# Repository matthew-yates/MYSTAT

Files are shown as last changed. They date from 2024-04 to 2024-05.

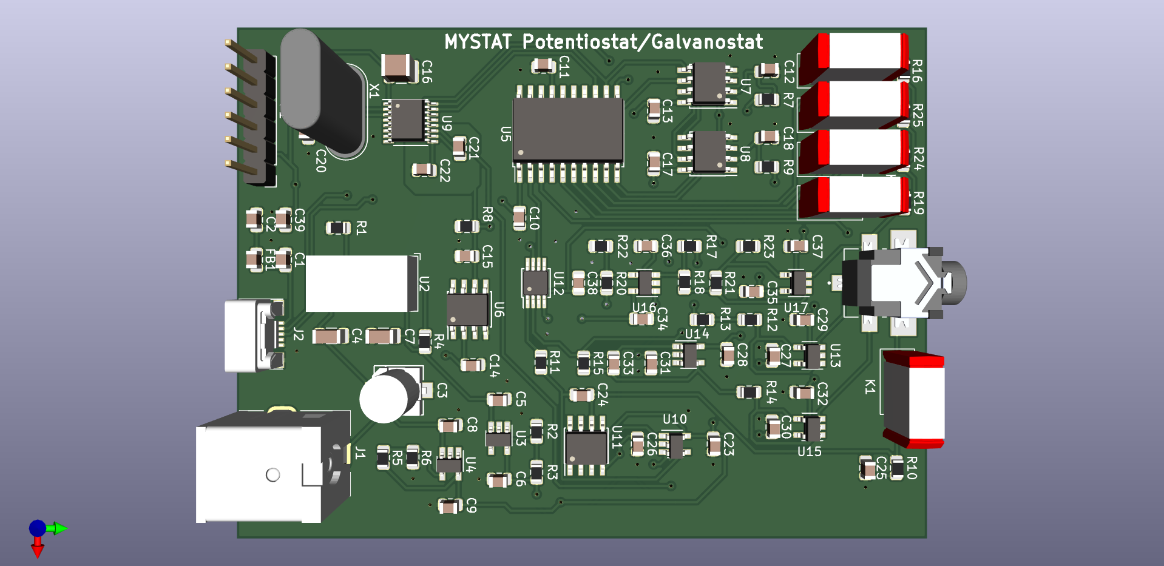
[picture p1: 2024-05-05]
hardware/mystat_circuit_board/mystat.png

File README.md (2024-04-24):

## MYSTAT Potentiostat/Galvanostat

These are the design files for building and operating a compact open source potentiostat/galvanostat instrument.  The detailed technical specifications and instructions for operation can be found in the HardwareX article [MYSTAT: A compact potentiostat/galvanostat for general electrochemistry measurements](https://www.hardware-x.com/article/S2468-0672(20)30072-9/fulltext). The HardwareX article has a link to a static repository at [Zenodo](https://zenodo.org/records/4252476).  This github repository was created as a clone of the Zenodo repository, with the goal of facilitating the tracking of improvements to hardware design and development of control software.

The MYSTAT instrument design and control software is based on an earlier open source design published by [Thomas Dobbelaere](https://www.hardware-x.com/article/S2468-0672(17)30031-7/fulltext), who also created a [github repository](https://github.com/thomasdob/tdstatv3) for that instrument.

The voltage and current ranges of MYSTAT are significantly higher than the original design of Dobbelaere. The printed circuit board was completely redesigned. Only relatively minor changes were made to the Python control software and microcontroller firmware originally created by Dobbelaere.

This hardware and control software is fully open source, and changes/improvements are welcome.  An entirely open source tool chain was used for its development (KiCad, Python, and Linux).

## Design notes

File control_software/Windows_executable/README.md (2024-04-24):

This Windows executable version of the control software includes Python 3 and all the supported libraries and modules needed.  The libusbK Windows device driver must also be installed.  Windows version 7 or later is required.

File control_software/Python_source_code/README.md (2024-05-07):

### Setup instructions for Python virtual environment

The current version of mystat.py is incompatible with the latest version of pyqtgraph.  As a workaround, set up a virtual environment that uses pyqtgraph version 0.12.4.  The code below can be followed to set up the virtual environment in the same directory (folder) that you have saved the file "mystat.py".

```
python3 -m venv venv
source venv/bin/activate
pip install pyqtgraph==0.12.4
pip install scipy
pip install PyQt5
pip install pyusb
deactivate
```

For Linux: To give users the ability to control the potentiostat without root permissions, make sure that the user is a member of the "plugdev" group.  Next, create a file named `/etc/udev/rules.d/99-mystat.rules` containing the line:

```
SUBSYSTEM=="usb", ATTRS{idVendor}=="a0a0", ATTRS{idProduct}=="0002", GROUP="plugdev", MODE="0666"
```

For Windows: The libusbK device driver must first be installed.

Each time you wish to run from source, you will need to use the virtual environment that uses pyqtgraph version 0.12.4.  Change to the directory that has "mystat.py" file saved and the venv created following instructions above.  Then, execute the code below to run from source.

```
source venv/bin/activate
python3 mystat.py
deactivate
```

Hopefully we will get the source code fixed to run with the latest version of pyqtgraph.

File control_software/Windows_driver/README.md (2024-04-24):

To install the USB drivers in Windows, you must have Windows version 7 or later.  Run the program Zadig.exe.  The potentiostat should appear in the device list as "USB potentiostat/galvanostat".  Install the driver named "libusbK".

More information on Zadig can be found from its authors at: [https://zadig.akeo.ie/](https://zadig.akeo.ie/)

Zadig is based on libwdi and is licensed under GPLv3.  The libwdi source code is included here as a zip compressed archive. The Zadig source code is found in the examples directory of the libwdi archive.

Alternatively, the latest version of the source code may be downloaded from the [github repository](https://github.com/pbatard/libwdi).

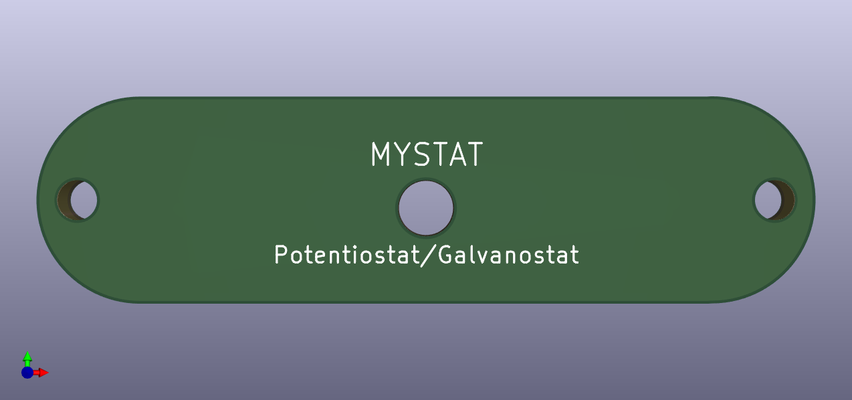
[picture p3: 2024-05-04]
hardware/frontpanel/frontpanel.png

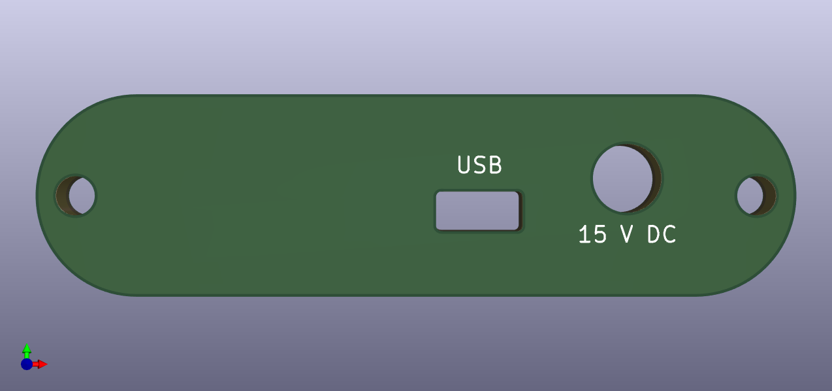
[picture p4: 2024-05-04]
hardware/backpanel/backpanel.png

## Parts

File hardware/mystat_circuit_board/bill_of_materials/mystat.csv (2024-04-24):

References | Manufacturer | Part Number | Value | Footprint | Quantity | Price(each) | Source
C1, C22 | KEMET | C0805C103J5GACTU | 10 nF | C_0805_2012Metric | 2 | 0.76 | Digikey ‎399-7992-1-ND‎
C16 | Samsung Electro-Mechanics | CL32B106KBJNNWE | 10 µF | C_1210_3225Metric | 1 | 0.66 | Digikey ‎1276-3388-1-ND‎
C19, C20, C33, C38 | Yageo | CC0805JRNPO9BN120 | 12 pF | C_0805_2012Metric | 4 | 0.11 | Digikey ‎311-1100-1-ND‎
C2, C10, C11, C12, C13, C14, C15, C17, C18, C23, C25, C26, C27, C28, C29, C30, C31, C32, C34, C35, C36, C37 | AVX Corporation | 08055C104KAT2A | 0.1 µF | C_0805_2012Metric | 22 | 0.15 | Digikey ‎478-1395-1-ND
C21 | Murata Electronics North America | GRM2165C1H332JA01D | 3.3 nF | C_0805_2012Metric | 1 | 0.25 | Digikey ‎490-1632-1-ND‎
C24 | Yageo | CC0805KRX7R9BB472 | 4700 pF | C_0805_2012Metric | 1 | 0.11 | Digikey ‎311-1133-1-ND‎
C3 | Panasonic Electronic Components | EEE-FT1V470AR | 47 μF | EEE-FT1V470AR | 1 | 0.5 | Digikey ‎PCE5014CT-ND‎
C4, C7 | Samsung Electro-Mechanics | CL31B475KBHNNNE | 4.7 μF | C_1206_3216Metric | 2 | 0.36 | Digikey ‎1276-2789-1-ND‎
C5, C6, C8, C9, C39 | TDK Corporation | C2012X7R1V475K125AC | 4.7 µF | C_0805_2012Metric | 5 | 0.73 | Digikey ‎445-7555-1-ND‎
FB1 | Vishay Dale | ILBB0805ER320V | Ferrite_Bead | C_0805_2012Metric | 1 | 0.1 | Digikey 541-2296-1-ND‎
J1 | CUI Inc. | PJ-063AH | PJ-063AH | CUI_PJ-063AH | 1 | 1.36 | ‎Digikey CP-063AH-ND‎
J2 | TE Connectivity AMP Connectors | 2173157-3 | 2173157-3 | CONN_2173157-3 | 1 | 3.39 | Digikey A124356CT-ND‎
J3 | CUI Inc. | SJ1-42534-SMT-TR | SJ1-42534-SMT | CUI_SJ1-42534-SMT | 1 | 1.2 | Digikey CP1-42534SJCT-ND
K1, K2, K3, K4, K5 | Coto Technology | 9011-05-11 | 9011-05-11 | relay_9011-05-11 | 5 | 7.97 | Digikey 306-1131-ND‎
P1 | Sullins Connector Solutions | PRPC006SAAN-RC | ICSP | PinHeader_1x06_P2.54mm_Vertical | 1 | 0.19 | Digikey S1011EC-06-ND‎
R1 | Panasonic Electronic Components | ERJ-6ENF6042V | 60.4 kΩ | R_0805_2012Metric | 1 | 0.1 | Digikey P60.4KCCT-ND‎
R10 | Panasonic Electronic Components | ERJ-6ENF27R0V | 27R | R_0805_2012Metric | 1 | 0.1 | Digikey P27.0CCT-ND‎
R12, R14 | Panasonic Electronic Components | ERA-6AEB4023V | 402k* | R_0805_2012Metric | 2 | 0.36 | Digikey P402KDACT-ND‎
R13, R15, R17, R18, R20, R22 | Panasonic Electronic Components | ERA-6AEB753V | 75k* | R_0805_2012Metric | 6 | 0.36 | Digikey P75KDACT-ND
R16 | Panasonic Electronic Components | ERA-6AEB104V | 100k* | R_0805_2012Metric | 1 | 0.36 | Digikey P100KDACT-ND
R19 | Panasonic Electronic Components | ERA-6AEB102V | 1k* | R_0805_2012Metric | 1 | 0.36 | Digikey P18KDACT-ND
R2 | Panasonic Electronic Components | ERA-6AEB8871V | 8.87 kΩ* | R_0805_2012Metric | 1 | 0.36 | Digikey P8.87KDACT-ND‎
R21 | Panasonic Electronic Components | ERA-6AEB183V | 18k* | R_0805_2012Metric | 1 | 0.36 | Digikey P18KDACT-ND
R23 | Panasonic Electronic Components | ERA-6AEB202V | 2k* | R_0805_2012Metric | 1 | 0.36 | Digikey P2.0KDACT-ND‎
R24 | TE Connectivity Passive Product | 2-1625868-7 | 10R* | R_0805_2012Metric | 1 | 0.53 | Digikey A110351CT-ND
R25 | Susumu | RL1220S-1R0-F | 1R* | R_0805_2012Metric | 1 | 0.33 | Digikey RL12S1.00FCT-ND
R3 | Panasonic Electronic Components | ERJ-PB6B8872V | 88.7 kΩ* | R_0805_2012Metric | 1 | 0.36 | Digikey P20816CT-ND
R4 | Panasonic Electronic Components | ERJ-6ENF1783V | 178 kΩ | R_0805_2012Metric | 1 | 0.1 | Digikey ‎P178KCCT-ND‎
R5 | Panasonic Electronic Components | ERJ-PB6B2943V | 294 kΩ* | R_0805_2012Metric | 1 | 0.36 | Digikey P20873CT-ND‎
R6 | Panasonic Electronic Components | ERJ-PB6B1743V | 174 kΩ* | R_0805_2012Metric | 1 | 0.36 | Digikey P20847CT-ND‎
R7, R9 | Yageo | RC0805FR-071KL | 1k | R_0805_2012Metric | 2 | 0.1 | Digikey 311-1.00KCRCT-ND
R8, R11 | Yageo | RC0805FR-0710KL | 10k | R_0805_2012Metric | 2 | 0.1 | Digikey 311-10.0KCRCT-ND‎
U10, U13, U14, U15, U16, U17 | Texas Instruments | OPA192IDBVR | OPA192 | OPA192 | 6 | 2.68 | Digikey 296-42105-1-ND‎
U11 | Texas Instruments | BUF634AIDR | BUF634A | SOIC-8 | 1 | 2.92 | Digikey 296-53619-1-ND‎
U12 | Analog Devices Inc. | ADG1419BRMZ-REEL7 | ADG1419 | MSOP-8_3x3mm_P0.65mm | 1 | 4.53 | Digikey ADG1419BRMZ-REEL7CT-ND‎
U2 | Linear Technology/Analog Devices | LTM8045IY | LTM8045 | BGA-40_6.25x11.25mm_Layout5x8_P1.25mm | 1 | 21.07 | Digikey LTM8045IY-ND‎
U3 | Analog Devices Inc. | ADP7182AUJZ-R7 | ADP7182AUJZ-R7 | TSOT-23-5 | 1 | 3.71 | Digikey ADP7182AUJZ-R7CT-ND‎
U4 | Analog Devices Inc. | ADP7118AUJZ-5.0-R7 | ADP7118AUJZ-5.0-R7 | TSOT-23-5 | 1 | 2.27 | Digikey ADP7118AUJZ-5.0-R7CT-ND
U5 | Microchip Technology | PIC16F1459-I/SO | PIC16F1459 | SOIC-20W | 1 | 1.77 | Digikey PIC16F1459-I/SO-ND‎
U6 | Analog Devices Inc. | ADR421ARZ | ADR421 | SOIC-8 | 1 | 6.81 | Digikey ‎ADR421ARZ-REEL7CT-ND
U7, U8 | Microchip Technology | MCP3550-60E/SN | MCP3550-60 | SOIC-8 | 2 | 3.98 | Digikey MCP3550-60E/SN-ND‎
U9 | Texas Instruments | DAC1220E | DAC1220 | DAC1220 | 1 | 19.8 | Digikey DAC1220E-ND‎
X1 | ECS Inc. | ECS-25-S-1X | 2.5 MHz | Crystal_HC49-U_Vertical | 1 | 1.13 | Digikey X1003-ND‎
E1 | Tensility International | 10-00340 | N.A. | N.A. | 1 | 4.44 | Digikey ‎839-1035-ND
E2 | Cinch Connectivity Solutions Johnson | 105-0302-001 | N.A. | N.A. | 1 | 1.14 | Digikey J103-ND
E3 | Cinch Connectivity Solutions Johnson | 105-0303-001 | N.A. | N.A. | 1 | 1.28 | Digikey J104-ND
E4 | Cinch Connectivity Solutions Johnson | 105-0304-001 | N.A. | N.A. | 1 | 1.17 | Digikey J301-ND
E5 | Cinch Connectivity Solutions Johnson | 105-0301-001 | N.A. | N.A. | 1 | 1.17 | Digikey J300-ND
E6-E9 | Cal Test Electronics | CT3759-0 | N.A. | N.A. | 4 | 2 | Digikey CT3759-0-ND
E10 | CUI Inc. | SDI30-15-U-P5 | N.A. | N.A. | 1 | 17.88 | Digikey 102-4106-ND
E11 | Hammond Manufacturing | 1455B802 | N.A. | N.A. | 1 | 9.6 | Digikey HM1117-ND
E12 | CUI Devices | AC-C13 NA | N.A. | N.A. | 1 | 3.76 | Digikey T1249-C13-NA-ND

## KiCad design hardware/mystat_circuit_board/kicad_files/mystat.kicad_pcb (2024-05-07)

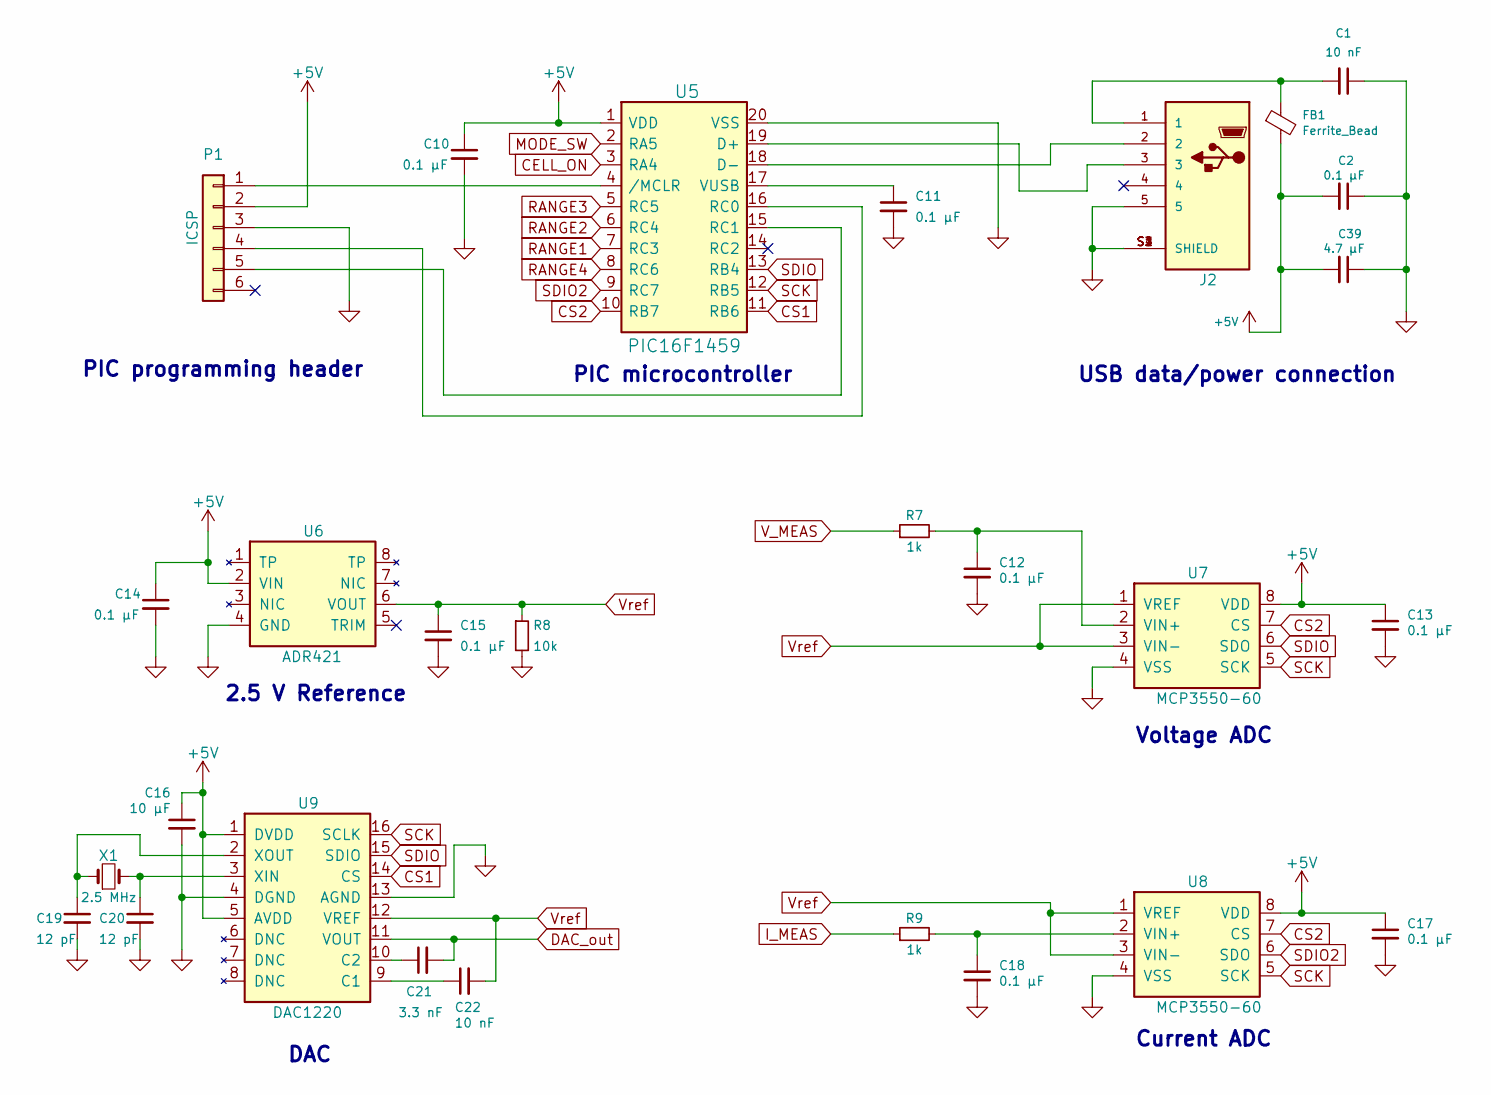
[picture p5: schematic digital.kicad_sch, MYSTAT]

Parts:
C1, C22: 10 nF; C_0805_2012Metric; Part Number C0805C103J5GACTU
C2, C10, C11, C12, C13, C14, C15, C17, C18: 0.1 µF; C_0805_2012Metric; Part Number 08055C104KAT2A
C16: 10 µF; C_1210_3225Metric; Part Number CL32B106KBJNNWE
C19, C20: 12 pF; C_0805_2012Metric; Part Number CC0805JRNPO9BN120
C21: 3.3 nF; C_0805_2012Metric; Part Number GRM2165C1H332JA01D
C39: 4.7 µF; C_0805_2012Metric; Part Number C2012X7R1V475K125AC
FB1: Ferrite_Bead; C_0805_2012Metric; Part Number ILBB0805ER320V
J2: 2173157-3; CONN_2173157-3; Part Number 2173157-3
P1: ICSP; PinHeader_1x06_P2.54mm_Vertical; Part Number PRPC006SAAN-RC
R7, R9: 1k; R_0805_2012Metric; Part Number RC0805FR-071KL
R8: 10k; R_0805_2012Metric; Part Number RC0805FR-0710KL
U5: PIC16F1459; SOIC-20W; Part Number PIC16F1459-I/SO
U6: ADR421; SOIC-8; Part Number ADR421ARZ
U7, U8: MCP3550-60; SOIC-8; Part Number MCP3550-60E/SN
U9: DAC1220; Part Number DAC1220E
X1: 2.5 MHz; Crystal_HC49-U_Vertical; Part Number ECS-25-S-1X

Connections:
+5V: C2.2, C10.1, C13.1, C14.1, C16.1, C17.1, C39.2, FB1.2, P1.2, U5.1 (VDD), U6.2 (VIN), U7.8 (VDD), U8.8 (VDD), U9.1 (DVDD), U9.5 (AVDD)
CELL_ON: U5.3 (RA4); also elsewhere on the board
CS1: U5.11 (RB6), U9.14 (CS)
CS2: U5.10 (RB7), U7.7 (CS), U8.7 (CS)
DAC_out: C21.2, U9.11 (VOUT); also elsewhere on the board
GND: C1.1, C2.1, C10.2, C11.2, C12.2, C13.2, C14.2, C15.2, C16.2, C17.2, C18.2, C19.2, C20.2, C39.1, J2.5, J2.S1 (SHIELD), J2.S2 (SHIELD), J2.S3 (SHIELD), J2.S4 (SHIELD), P1.3, R8.2, U5.20 (VSS), U6.4 (GND), U7.4 (VSS), U8.4 (VSS), U9.4 (DGND), U9.13 (AGND); also elsewhere on the board
I_MEAS: R9.1; also elsewhere on the board
MODE_SW: U5.2 (RA5); also elsewhere on the board
unnamed: C1.2, FB1.1, J2.1
unnamed: C11.1, U5.17 (VUSB)
unnamed: C12.1, R7.2, U7.2 (VIN+)
unnamed: C18.1, R9.2, U8.2 (VIN+)
unnamed: C19.1, U9.2 (XOUT), X1.1
unnamed: C20.1, U9.3 (XIN), X1.2
unnamed: C21.1, U9.10 (C2)
unnamed: C22.1, U9.9 (C1)
unnamed: J2.2, U5.18 (D-)
unnamed: J2.3, U5.19 (D+)
unnamed: P1.1, U5.4 (/MCLR)
unnamed: P1.4, U5.16 (RC0)
unnamed: P1.5, U5.15 (RC1)
RANGE1: U5.7 (RC3); also elsewhere on the board
RANGE2: U5.6 (RC4); also elsewhere on the board
RANGE3: U5.5 (RC5); also elsewhere on the board
RANGE4: U5.8 (RC6); also elsewhere on the board
SCK: U5.12 (RB5), U7.5 (SCK), U8.5 (SCK), U9.16 (SCLK)
SDIO: U5.13 (RB4), U7.6 (SDO), U9.15 (SDIO)
SDIO2: U5.9 (RC7), U8.6 (SDO)
V_MEAS: R7.1; also elsewhere on the board
Vref: C15.1, C22.2, R8.1, U6.6 (VOUT), U7.1 (VREF), U7.3 (VIN-), U8.1 (VREF), U8.3 (VIN-), U9.12 (VREF); also elsewhere on the board

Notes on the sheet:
PIC programming header
PIC microcontroller
DAC
2.5 V Reference
Voltage ADC
USB data/power connection
Current ADC

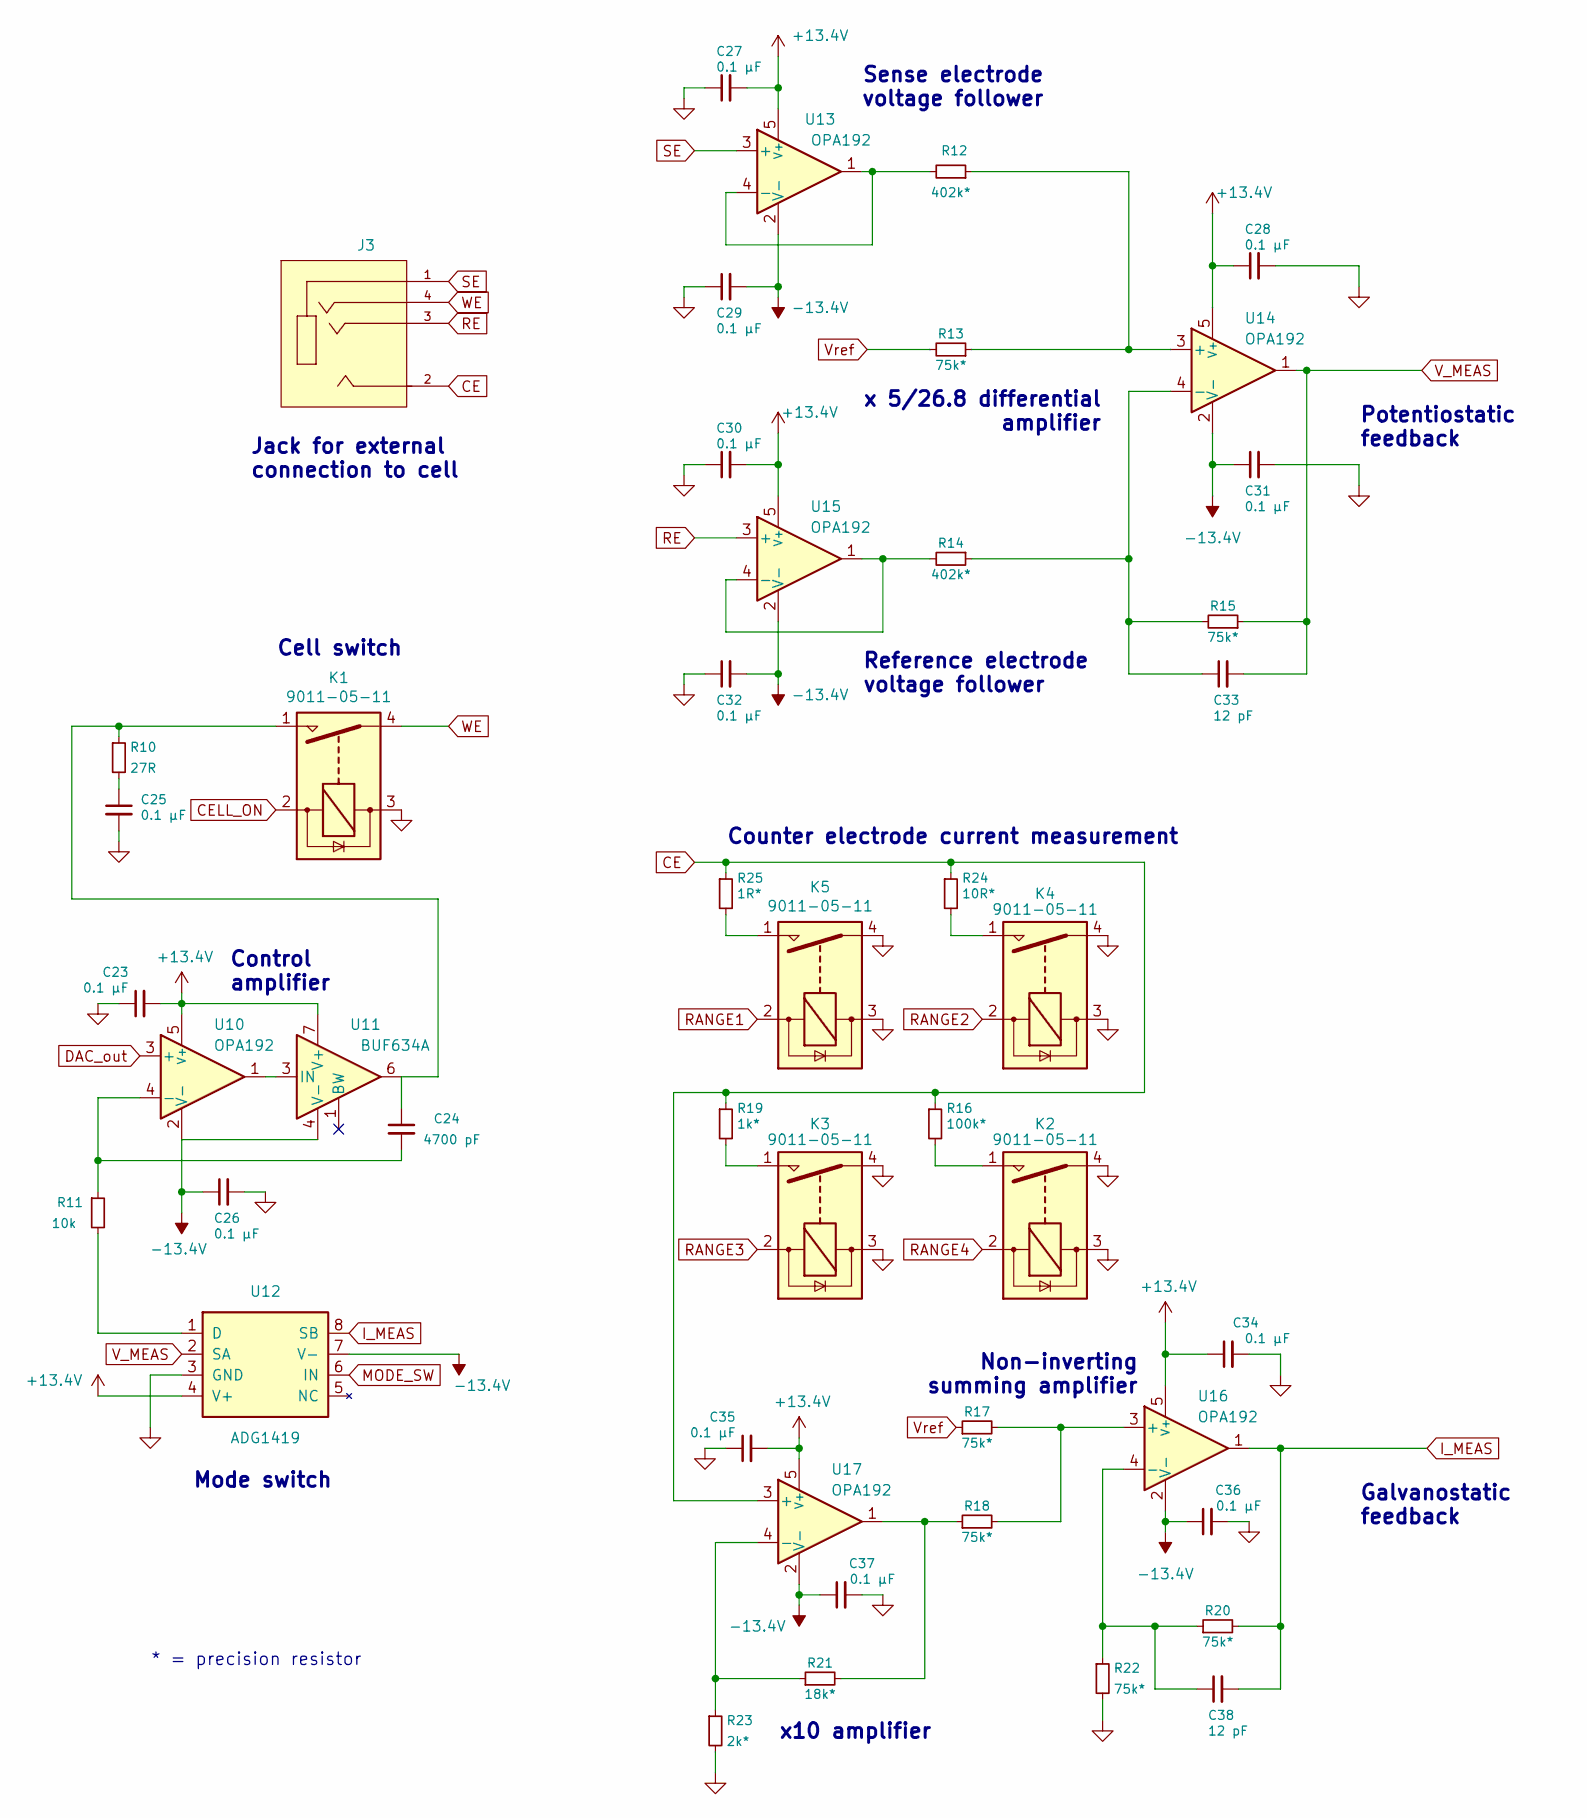
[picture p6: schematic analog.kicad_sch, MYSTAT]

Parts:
C23, C25, C26, C27, C28, C29, C30, C31, C32, C34, C35, C36, C37: 0.1 µF; C_0805_2012Metric; Part Number 08055C104KAT2A
C24: 4700 pF; C_0805_2012Metric; Part Number CC0805KRX7R9BB472
C33, C38: 12 pF; C_0805_2012Metric; Part Number CC0805JRNPO9BN120
J3: SJ1-42534-SMT; CUI_SJ1-42534-SMT; Part Number SJ1-42534-SMT-TR
K1, K2, K3, K4, K5: 9011-05-11; relay_9011-05-11; Part Number 9011-05-11
R10: 27R; R_0805_2012Metric; Part Number ERJ-6ENF27R0V
R11: 10k; R_0805_2012Metric; Part Number RC0805FR-0710KL
R12, R14: 402k*; R_0805_2012Metric; Part Number ERA-6AEB4023V
R13, R15, R17, R18, R20, R22: 75k*; R_0805_2012Metric; Part Number ERA-6AEB753V
R16: 100k*; R_0805_2012Metric; Part Number ERA-6AEB104V
R19: 1k*; R_0805_2012Metric; Part Number ERA-6AEB102V
R21: 18k*; R_0805_2012Metric; Part Number ERA-6AEB183V
R23: 2k*; R_0805_2012Metric; Part Number ERA-6AEB202V
R24: 10R*; R_0805_2012Metric; Part Number 2-1625868-7
R25: 1R*; R_0805_2012Metric; Part Number RL1220S-1R0-F
U10, U13, U14, U15, U16, U17: OPA192; Part Number OPA192IDBVR
U11: BUF634A; SOIC-8; Part Number BUF634AIDR
U12: ADG1419; MSOP-8_3x3mm_P0.65mm; Part Number ADG1419BRMZ-REEL7

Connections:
+13.4V: C23.2, C27.2, C28.1, C30.2, C34.1, C35.2, U10.5 (V+), U11.7 (V+), U12.4 (V+), U13.5 (V+), U14.5 (V+), U15.5 (V+), U16.5 (V+), U17.5 (V+); also elsewhere on the board
-13.4V: C26.1, C29.2, C31.1, C32.2, C36.1, C37.1, U10.2 (V-), U11.4 (V-), U12.7 (V-), U13.2 (V-), U14.2 (V-), U15.2 (V-), U16.2 (V-), U17.2 (V-); also elsewhere on the board
CE: J3.2, R16.1, R19.1, R24.1, R25.1, U17.3 (+)
CELL_ON: K1.2; also elsewhere on the board
DAC_out: U10.3 (+); also elsewhere on the board
GND: C23.1, C25.2, C26.2, C27.1, C28.2, C29.1, C30.1, C31.2, C32.1, C34.2, C35.1, C36.2, C37.2, K1.3, K2.3, K2.4, K3.3, K3.4, K4.3, K4.4, K5.3, K5.4, R22.2, R23.2, U12.3 (GND); also elsewhere on the board
I_MEAS: C38.2, R20.2, U12.8 (SB), U16.1; also elsewhere on the board
MODE_SW: U12.6 (IN); also elsewhere on the board
unnamed: C24.1, K1.1, R10.1, U11.6
unnamed: C24.2, R11.1, U10.4 (-)
unnamed: C25.1, R10.2
unnamed: C33.1, R14.1, R15.2, U14.4 (-)
unnamed: C38.1, R20.1, R22.1, U16.4 (-)
unnamed: K2.1, R16.2
unnamed: K3.1, R19.2
unnamed: K4.1, R24.2
unnamed: K5.1, R25.2
unnamed: R11.2, U12.1 (D)
unnamed: R12.1, R13.1, U14.3 (+)
unnamed: R12.2, U13.1, U13.4 (-)
unnamed: R14.2, U15.1, U15.4 (-)
unnamed: R17.2, R18.2, U16.3 (+)
unnamed: R18.1, R21.2, U17.1
unnamed: R21.1, R23.1, U17.4 (-)
unnamed: U10.1, U11.3 (IN)
RANGE1: K5.2; also elsewhere on the board
RANGE2: K4.2; also elsewhere on the board
RANGE3: K3.2; also elsewhere on the board
RANGE4: K2.2; also elsewhere on the board
RE: J3.3, U15.3 (+)
SE: J3.1, U13.3 (+)
V_MEAS: C33.2, R15.1, U12.2 (SA), U14.1; also elsewhere on the board
Vref: R13.2, R17.1; also elsewhere on the board
WE: J3.4, K1.4

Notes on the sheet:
Sense electrode voltage follower
Mode switch
x10 amplifier
Galvanostatic feedback
Non-inverting summing amplifier
* = precision resistor
Counter electrode current measurement
x 5/26.8 differential amplifier
Reference electrode voltage follower
Control amplifier
Cell switch
Potentiostatic feedback
Jack for external connection to cell

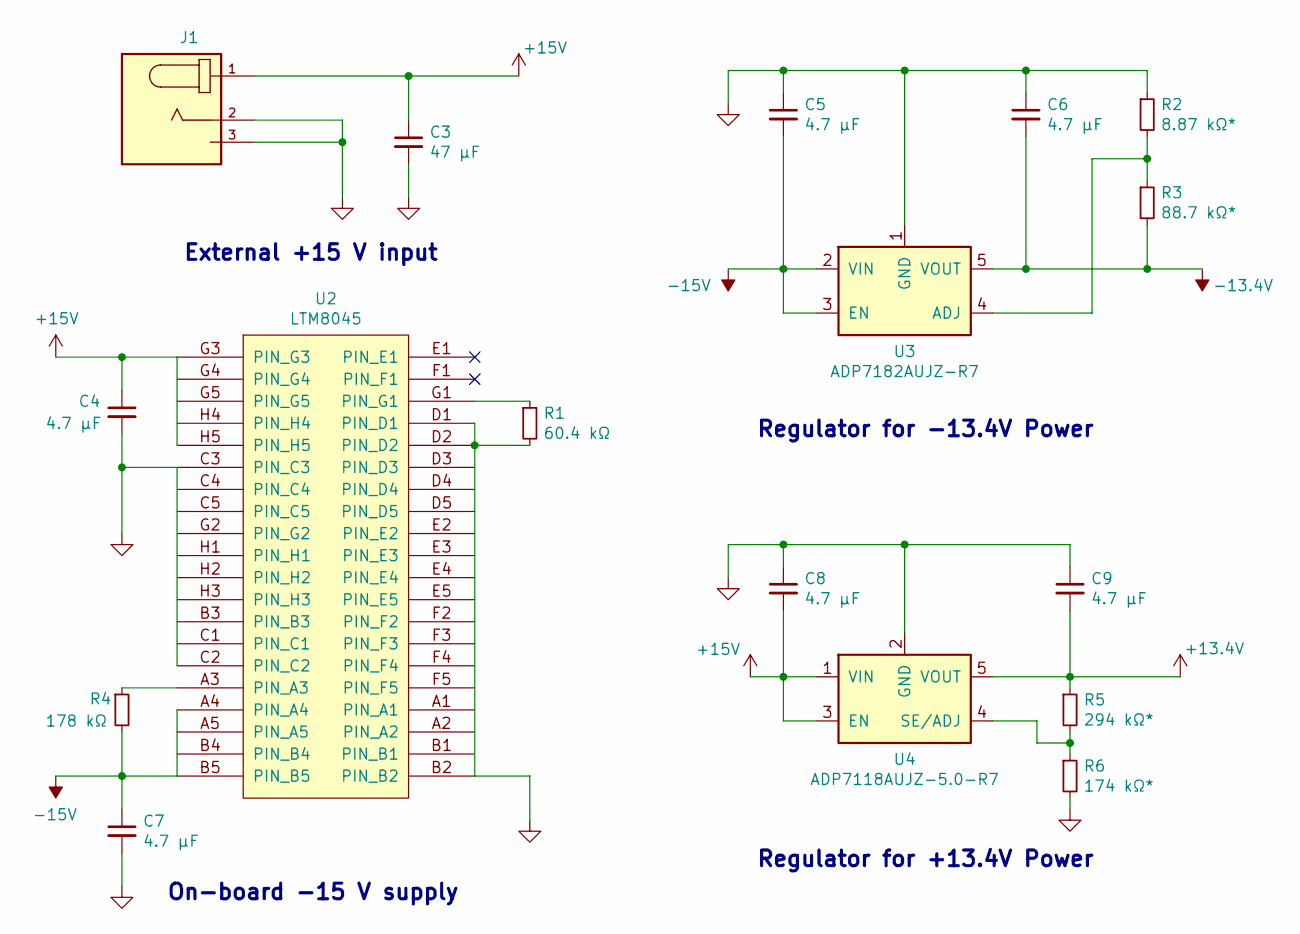
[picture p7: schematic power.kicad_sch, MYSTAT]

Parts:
C3: 47 μF; EEE-FT1V470AR; Part Number EEE-FT1V470AR
C4, C7: 4.7 μF; C_1206_3216Metric; Part Number CL31B475KBHNNNE
C5, C6, C8, C9: 4.7 µF; C_0805_2012Metric; Part Number C2012X7R1V475K125AC
J1: PJ-063AH; CUI_PJ-063AH; Part Number PJ-063AH
R1: 60.4 kΩ; R_0805_2012Metric; Part Number ERJ-6ENF6042V
R2: 8.87 kΩ*; R_0805_2012Metric; Part Number ERA-6AEB8871V
R3: 88.7 kΩ*; R_0805_2012Metric; Part Number ERJ-PB6B8872V
R4: 178 kΩ; R_0805_2012Metric; Part Number ERJ-6ENF1783V
R5: 294 kΩ*; R_0805_2012Metric; Part Number ERJ-PB6B2943V
R6: 174 kΩ*; R_0805_2012Metric; Part Number ERJ-PB6B1743V
U2: LTM8045; MODULE; Part Number LTM8045IY
U3: ADP7182AUJZ-R7; TSOT-23-5; Part Number ADP7182AUJZ-R7
U4: ADP7118AUJZ-5.0-R7; TSOT-23-5; Part Number ADP7118AUJZ-5.0-R7

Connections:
+13.4V: C9.2, R5.1, U4.5 (VOUT); also elsewhere on the board
+15V: C3.1, C4.1, C8.2, J1.1, U2.G3 (PIN_G3), U2.G4 (PIN_G4), U2.G5 (PIN_G5), U2.H4 (PIN_H4), U2.H5 (PIN_H5), U4.1 (VIN), U4.3 (EN)
-13.4V: C6.2, R3.2, U3.5 (VOUT); also elsewhere on the board
-15V: C5.2, C7.1, R4.2, U2.A4 (PIN_A4), U2.A5 (PIN_A5), U2.B4 (PIN_B4), U2.B5 (PIN_B5), U3.2 (VIN), U3.3 (EN)
GND: C3.2, C4.2, C5.1, C6.1, C7.2, C8.1, C9.1, J1.2, J1.3 (SHIELD), R1.2, R2.1, R6.2, U2.A1 (PIN_A1), U2.A2 (PIN_A2), U2.B1 (PIN_B1), U2.B2 (PIN_B2), U2.B3 (PIN_B3), U2.C1 (PIN_C1), U2.C2 (PIN_C2), U2.C3 (PIN_C3), U2.C4 (PIN_C4), U2.C5 (PIN_C5), U2.D1 (PIN_D1), U2.D2 (PIN_D2), U2.D3 (PIN_D3), U2.D4 (PIN_D4), U2.D5 (PIN_D5), U2.E2 (PIN_E2), U2.E3 (PIN_E3), U2.E4 (PIN_E4), U2.E5 (PIN_E5), U2.F2 (PIN_F2), U2.F3 (PIN_F3), U2.F4 (PIN_F4), U2.F5 (PIN_F5), U2.G2 (PIN_G2), U2.H1 (PIN_H1), U2.H2 (PIN_H2), U2.H3 (PIN_H3), U3.1 (GND), U4.2 (GND); also elsewhere on the board
unnamed: R1.1, U2.G1 (PIN_G1)
unnamed: R2.2, R3.1, U3.4 (ADJ)
unnamed: R4.1, U2.A3 (PIN_A3)
unnamed: R5.2, R6.1, U4.4 (SE/ADJ)

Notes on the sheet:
Regulator for -13.4V Power
Regulator for +13.4V Power
On-board -15 V supply
External +15 V input

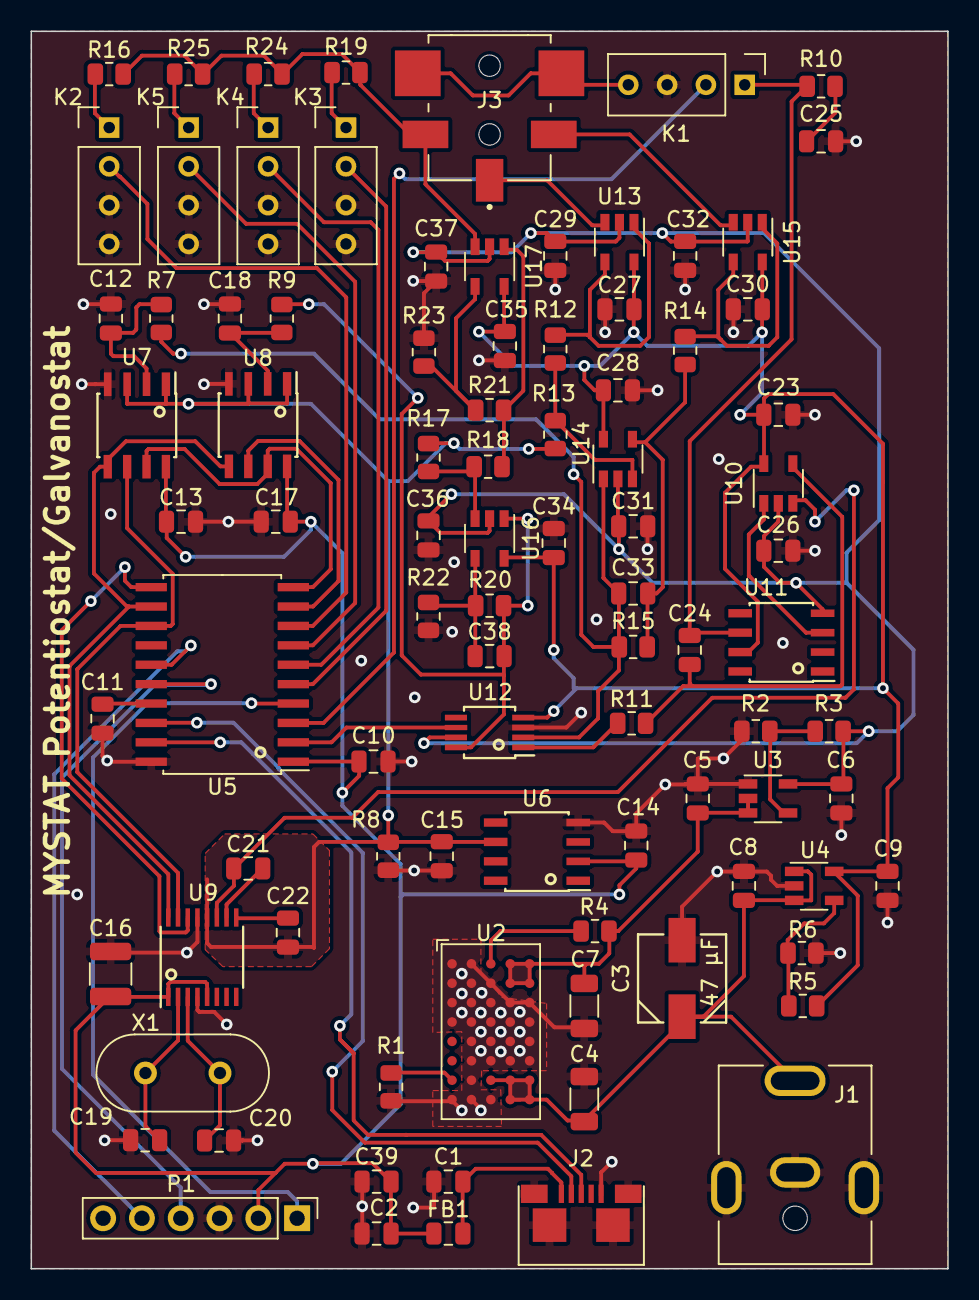
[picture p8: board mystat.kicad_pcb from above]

Board: 4 copper layers, 60.0 x 81.0 mm, 91 parts (0 on the bottom side), 59 nets.

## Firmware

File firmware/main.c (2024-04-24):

/*
 * USB Potentiostat/galvanostat firmware
 *
 * This code makes use of Signal 11's M-Stack USB stack to implement 
 * communication through raw USB bulk transfers. Commands are received
 * as ASCII strings on EP1 OUT. They are then interpreted and executed;
 * they either change the state of output pins, or cause data to be read
 * from / written to the MCP3550 (ADC) or DAC1220 (DAC) using a software
 * SPI implementation. The resulting data, or an "OK" message, is sent as
 * a reply on EP1 IN. The USB service is interrupt-driven.
 *
 * Thomas Dobbelaere
 * CoCooN research group
 * 2016-06-07
 */

#include "usb.h"
#include <xc.h>
#include <string.h>
#include "usb_config.h"
#include "usb_ch9.h"
#include "spi_software.h"
#include "Flash.h"
#include "HEFlash.h"

// PIC16F1459 configuration bit settings:
// CONFIG1
#pragma config FOSC = INTOSC    // Oscillator Selection Bits (INTOSC oscillator: I/O function on CLKIN pin)
#pragma config WDTE = OFF       // Watchdog Timer Enable (WDT disabled)
#pragma config PWRTE = OFF      // Power-up Timer Enable (PWRT disabled)
#pragma config MCLRE = OFF      // MCLR Pin Function Select (MCLR/VPP pin function is digital input)
#pragma config CP = OFF         // Flash Program Memory Code Protection (Program memory code protection is disabled)
#pragma config BOREN = ON       // Brown-out Reset Enable (Brown-out Reset enabled)
#pragma config CLKOUTEN = OFF   // Clock Out Enable (CLKOUT function is disabled. I/O or oscillator function on the CLKOUT pin)
#pragma config IESO = OFF       // Internal/External Switchover Mode (Internal/External Switchover Mode is disabled)
#pragma config FCMEN = OFF      // Fail-Safe Clock Monitor Enable (Fail-Safe Clock Monitor is disabled)

// CONFIG2
#pragma config WRT = OFF        // Flash Memory Self-Write Protection (Write protection off)
#pragma config CPUDIV = NOCLKDIV// CPU System Clock Selection Bit (NO CPU system divide)
#pragma config USBLSCLK = 48MHz // USB Low Speed Clock Selection bit (System clock expects 48 MHz, FS/LS USB CLKENs divide-by is set to 8.)
#pragma config PLLMULT = 3x     // PLL Multipler Selection Bit (3x Output Frequency Selected)
#pragma config PLLEN = ENABLED  // PLL Enable Bit (3x or 4x PLL Enabled)
#pragma config STVREN = ON      // Stack Overflow/Underflow Reset Enable (Stack Overflow or Underflow will cause a Reset)
#pragma config BORV = LO        // Brown-out Reset Voltage Selection (Brown-out Reset Voltage (Vbor), low trip point selected.)
#pragma config LPBOR = OFF      // Low-Power Brown Out Reset (Low-Power BOR is disabled)
#pragma config LVP = ON        // Low-Voltage Programming Enable (High-voltage on MCLR/VPP must be used for programming)

#define _XTAL_FREQ 48000000     // 48 MHz CPU clock frequency

#define MODE_SW_PIN LATAbits.LATA5
#define MODE_SW_TRIS TRISAbits.TRISA5
#define CELL_ON_PIN LATAbits.LATA4
#define CELL_ON_TRIS TRISAbits.TRISA4
#define CELL_ON  1
#define CELL_OFF 0
#define POTENTIOSTATIC  0
#define GALVANOSTATIC  1
#define INPUT  1
#define OUTPUT 0
#define RANGE1_PIN LATCbits.LATC3
#define RANGE1_TRIS TRISCbits.TRISC3
#define RANGE2_PIN LATCbits.LATC4
#define RANGE2_TRIS TRISCbits.TRISC4
#define RANGE3_PIN LATCbits.LATC5
#define RANGE3_TRIS TRISCbits.TRISC5
#define RANGE4_PIN LATCbits.LATC6
#define RANGE4_TRIS TRISCbits.TRISC6

static const uint8_t* received_data;
static uint8_t received_data_length;
static uint8_t* transmit_data;
static uint8_t transmit_data_length;
static uint8_t heflashbuffer[FLASH_ROWSIZE];

void InitializeIO()
{
	OSCCONbits.IRCF = 0b1111; // 0b1111 = 16MHz HFINTOSC postscaler
	ANSELA = 0x00; // digital I/O on PORTA
	ANSELB = 0x00; // digital I/O on PORTB
	ANSELC = 0x00; // digital I/O on PORTC
	APFCON = 0x00; // no funny alternate pins
	MODE_SW_TRIS = OUTPUT;
	MODE_SW_PIN = POTENTIOSTATIC; // initialize mode to potentiostatic
	CELL_ON_TRIS = OUTPUT;
	CELL_ON_PIN = CELL_OFF; // initialize cell to off position
	RANGE1_TRIS = OUTPUT;
	RANGE2_TRIS = OUTPUT;
	RANGE3_TRIS = OUTPUT;
	RANGE4_TRIS = OUTPUT;
	RANGE1_PIN = 1; // initialize range to range 1
	RANGE2_PIN = 0;
	RANGE3_PIN = 0;
	RANGE4_PIN = 0;
	InitializeSPI();
	__delay_ms(25); // power-up delay - necessary for DAC1220
	DAC1220_Reset();
	__delay_ms(25);
	DAC1220_Init();
	HEFLASH_readBlock(heflashbuffer, 2, FLASH_ROWSIZE); // get dac calibration
	DAC1220_Write3Bytes(8, heflashbuffer[0], heflashbuffer[1], heflashbuffer[2]); // apply dac calibration
	DAC1220_Write3Bytes(12, heflashbuffer[3], heflashbuffer[4], heflashbuffer[5]); 
}

void command_unknown()
{
	const uint8_t* reply = "?";
    strcpy(transmit_data, reply);
    transmit_data_length = strlen(reply);
}

void send_OK()
{
	const uint8_t* reply = "OK";
    strcpy(transmit_data, reply);
    transmit_data_length = strlen(reply);
}

void command_cell_on()
{
	CELL_ON_PIN = CELL_ON;
	send_OK();
}

void command_cell_off()
{
	CELL_ON_PIN = CELL_OFF;
	send_OK();
}

void command_mode_potentiostatic()
{
	MODE_SW_PIN = POTENTIOSTATIC;
	send_OK();
}

void command_mode_galvanostatic()
{
	MODE_SW_PIN = GALVANOSTATIC;
	send_OK();
}

void command_range1()
{
    RANGE1_PIN = 1;
    __delay_ms(10); // make the new relay setting before breaking the old one
    RANGE2_PIN = 0;
    RANGE3_PIN = 0;
    RANGE4_PIN = 0;
	send_OK();
}

void command_range2()
{
    RANGE2_PIN = 1;
    __delay_ms(10); // make the new relay setting before breaking the old one
    RANGE1_PIN = 0;
    RANGE3_PIN = 0;
    RANGE4_PIN = 0;
	send_OK();
}

void command_range3()
{
    RANGE3_PIN = 1;
    __delay_ms(10); // make the new relay setting before breaking the old one
    RANGE1_PIN = 0;
    RANGE2_PIN = 0;
    RANGE4_PIN = 0;
	send_OK();
}

void command_range4()
{
    RANGE4_PIN = 1;
    __delay_ms(10); // make the new relay setting before breaking the old one
    RANGE1_PIN = 0;
    RANGE2_PIN = 0;
    RANGE3_PIN = 0;
	send_OK();
}

void command_set_dac(const uint8_t* dac_data)
{
	DAC1220_Write3Bytes(0, dac_data[0], dac_data[1], dac_data[2]);
	send_OK();
}

void command_calibrate_dac()
{
	DAC1220_SelfCal();
	__delay_ms(500); // wait until calibration is finished
	uint8_t data[6];
	DAC1220_Read3Bytes(8, data, data+1, data+2); // get calibration data
	DAC1220_Read3Bytes(12, data+3, data+4, data+5);
	HEFLASH_writeBlock(2, data, 6); // save calibration data to HEFLASH
	send_OK();
}

void command_read_adc()
{
	uint8_t adc_data[6];
	if(MCP3550_Read(adc_data))
	{
		transmit_data_length=6;
		memcpy(transmit_data, adc_data, transmit_data_length);
	}
	else
	{
		const uint8_t* reply = "WAIT";
		strcpy(transmit_data, reply);
		transmit_data_length = strlen(reply);
	}
}

void command_read_offset()
{
	HEFLASH_readBlock(heflashbuffer, 1, FLASH_ROWSIZE);
	transmit_data_length=6;
	memcpy(transmit_data, heflashbuffer, transmit_data_length);
}

void command_save_offset(const uint8_t* offset_data)
{
	HEFLASH_writeBlock(1, offset_data, 6);
	send_OK();
}

void command_read_shuntcalibration()
{
	HEFLASH_readBlock(heflashbuffer, 3, FLASH_ROWSIZE);
	transmit_data_length=8;
	memcpy(transmit_data, heflashbuffer, transmit_data_length);
}

void command_save_shuntcalibration(const uint8_t* shuntcalibration_data)
{
	HEFLASH_writeBlock(3, shuntcalibration_data, 8);
	send_OK();
}

void command_read_dac_cal()
{
	HEFLASH_readBlock(heflashbuffer, 2, FLASH_ROWSIZE);
	transmit_data_length=6;
	memcpy(transmit_data, heflashbuffer, transmit_data_length);
}

void command_set_dac_cal(const uint8_t* dac_cal_data)
{
	HEFLASH_writeBlock(2, dac_cal_data, 6);
	DAC1220_Write3Bytes(8, dac_cal_data[0], dac_cal_data[1], dac_cal_data[2]);
	DAC1220_Write3Bytes(12, dac_cal_data[3], dac_cal_data[4], dac_cal_data[5]);
	send_OK();
}

void interpret_command() {
    if (received_data_length == 7 && strncmp(received_data,"CELL ON",7) == 0)
        command_cell_on();
    else if (received_data_length == 8 && strncmp(received_data,"CELL OFF",8) == 0)
        command_cell_off();
    else if (received_data_length == 14 && strncmp(received_data,"POTENTIOSTATIC",14) == 0)
        command_mode_potentiostatic();
    else if (received_data_length == 13 && strncmp(received_data,"GALVANOSTATIC",13) == 0)
        command_mode_galvanostatic();
    else if (received_data_length == 7 && strncmp(received_data,"RANGE 1",7) == 0)
        command_range1();
    else if (received_data_length == 7 && strncmp(received_data,"RANGE 2",7) == 0)
        command_range2();
    else if (received_data_length == 7 && strncmp(received_data,"RANGE 3",7) == 0)
        command_range3();
    else if (received_data_length == 7 && strncmp(received_data,"RANGE 4",7) == 0)
        command_range4();
    else if (received_data_length == 10 && strncmp(received_data,"DACSET ",7) == 0)
	command_set_dac(received_data+7);
    else if (received_data_length == 6 && strncmp(received_data,"DACCAL",6) == 0)
	command_calibrate_dac();
    else if (received_data_length == 7 && strncmp(received_data,"ADCREAD",7) == 0)
	command_read_adc();
    else if (received_data_length == 10 && strncmp(received_data,"OFFSETREAD",10) == 0)
	command_read_offset();
    else if (received_data_length == 17 && strncmp(received_data,"OFFSETSAVE ",11) == 0)
	command_save_offset(received_data+11);
    else if (received_data_length == 9 && strncmp(received_data,"DACCALGET",9) == 0)
	command_read_dac_cal();
    else if (received_data_length == 16 && strncmp(received_data,"DACCALSET ",10) == 0)
	command_set_dac_cal(received_data+10);
    else if (received_data_length == 12 && strncmp(received_data,"SHUNTCALREAD",12) == 0)
	command_read_shuntcalibration();
    else if (received_data_length == 21 && strncmp(received_data,"SHUNTCALSAVE ",13) == 0)
	command_save_shuntcalibration(received_data+13);
    else
        command_unknown();
}

int main(void)
{
	InitializeIO();

	// Enable Active clock-tuning from the USB
	ACTCONbits.ACTSRC = 1; // 1=USB
	ACTCONbits.ACTEN = 1;

	// Configure interrupts
	INTCONbits.PEIE = 1;
	INTCONbits.GIE = 1;

	// Initialize USB
	usb_init();

	while (1)
	{
		if (usb_is_configured() && usb_out_endpoint_has_data(1)) // wait for data received from host
		{
			if (!usb_in_endpoint_halted(1))
			{
				while (usb_in_endpoint_busy(1)) // wait for EP1 IN to become free
					;
				received_data_length = usb_get_out_buffer(1, &received_data); // get memory location and length of received data
				transmit_data = usb_get_in_buffer(1); // get memory location of data to transmit
				interpret_command(); // this reads received_data and sets transmit_data and transmit_data_length
				usb_send_in_buffer(1, transmit_data_length); // send the data back
			}
			usb_arm_out_endpoint(1);
		}
	}

	return 0;
}

void interrupt isr()
{
	usb_service();
}

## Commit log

2024-04-24 Adding all files & folders under the project
    [analog.sch, backpanel-B.CrtYd.gbr, backpanel-B.Cu.gbl, backpanel-B.Fab.gbr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]
2024-05-04 Delete hardware/backpanel/kicad_files/backpanel.sch
    updating to new KiCad file formats
    [backpanel.sch]
2024-05-04 Add files via upload
    update to KiCad version 6.0 in Debian 12.5
    [backpanel.kicad_sch]
2024-05-04 Delete hardware/backpanel/kicad_files/backpanel.kicad_pcb
    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
    [backpanel.kicad_pcb]
2024-05-04 Add files via upload
    KiCad version 6.0 from Debian 12.5
    [backpanel.kicad_pcb]
2024-05-04 Add files via upload
    created with KiCad 6.0 from Debian 12.5
    [backpanel-B_Courtyard.gbr, backpanel-B_Cu.gbl, backpanel-B_Fab.gbr, backpanel-B_Mask.gbs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]
2024-05-04 Delete hardware/backpanel/gerber_files/backpanel-B.CrtYd.gbr
    replaced with new KiCad version
    [backpanel-B.CrtYd.gbr]
2024-05-04 Delete hardware/backpanel/gerber_files/backpanel-B.Cu.gbl
    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
    [backpanel-B.Cu.gbl]
2024-05-04 Delete hardware/backpanel/gerber_files/backpanel-B.Fab.gbr
    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
    [backpanel-B.Fab.gbr]
2024-05-04 Delete hardware/backpanel/gerber_files/backpanel-B.Mask.gbs
    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
    [backpanel-B.Mask.gbs]
2024-05-04 Delete hardware/backpanel/gerber_files/backpanel-B.Paste.gbp
    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
    [backpanel-B.Paste.gbp]
2024-05-04 Delete hardware/backpanel/gerber_files/backpanel-B.SilkS.gbo
    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
    [backpanel-B.SilkS.gbo]
2024-05-04 Delete hardware/backpanel/gerber_files/backpanel-Edge.Cuts.gm1
    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
    [backpanel-Edge.Cuts.gm1]
2024-05-04 Delete hardware/backpanel/gerber_files/backpanel-F.CrtYd.gbr
    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
    [backpanel-F.CrtYd.gbr]
2024-05-04 Delete hardware/backpanel/gerber_files/backpanel-F.Cu.gtl
    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
    [backpanel-F.Cu.gtl]
2024-05-04 Delete hardware/backpanel/gerber_files/backpanel-F.Fab.gbr
    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
    [backpanel-F.Fab.gbr]
2024-05-04 Delete hardware/backpanel/gerber_files/backpanel-F.Mask.gts
    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
    [backpanel-F.Mask.gts]
2024-05-04 Delete hardware/backpanel/gerber_files/backpanel-F.Paste.gtp
    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
    [backpanel-F.Paste.gtp]
2024-05-04 Delete hardware/backpanel/gerber_files/backpanel-F.SilkS.gto
    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
    [backpanel-F.SilkS.gto]
2024-05-04 Add files via upload
    Minor changes allowing KiCad design rules check to complete without error
    [backpanel-B_Courtyard.gbr, backpanel-B_Cu.gbl, backpanel-B_Fab.gbr, backpanel-B_Mask.gbs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]
2024-05-04 Add files via upload
    minor changes to allow KiCad design rules check to complete without errors or warnings
    [backpanel.kicad_pcb]
2024-05-04 Add files via upload
    PCB image from KiCad 6.0 3D viewer
2024-05-04 Delete hardware/frontpanel/kicad_files/frontpanel.kicad_pcb
    replaced with file from KiCad 6.0 from Debian 12.5
    [frontpanel.kicad_pcb]
2024-05-04 Delete hardware/frontpanel/kicad_files/frontpanel.sch
    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
    [frontpanel.sch]
2024-05-04 Add files via upload
    update to KiCad 6.0 from Debian 12.5
    [frontpanel.kicad_pcb, frontpanel.kicad_sch]
2024-05-04 Delete hardware/frontpanel/gerber_files/frontpanel-B.CrtYd.gbr
    replaced with files created in KiCad 6.0 from Debian 12.5
    [frontpanel-B.CrtYd.gbr]
2024-05-04 Delete hardware/frontpanel/gerber_files/frontpanel-B.Cu.gbl
    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
    [frontpanel-B.Cu.gbl]
2024-05-04 Delete hardware/frontpanel/gerber_files/frontpanel-B.Fab.gbr
    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
    [frontpanel-B.Fab.gbr]
2024-05-04 Delete hardware/frontpanel/gerber_files/frontpanel-B.Mask.gbs
    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
    [frontpanel-B.Mask.gbs]
2024-05-04 Delete hardware/frontpanel/gerber_files/frontpanel-B.Paste.gbp
    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
    [frontpanel-B.Paste.gbp]
2024-05-04 Delete hardware/frontpanel/gerber_files/frontpanel-B.SilkS.gbo
    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
    [frontpanel-B.SilkS.gbo]
2024-05-04 Delete hardware/frontpanel/gerber_files/frontpanel-Edge.Cuts.gm1
    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
    [frontpanel-Edge.Cuts.gm1]
2024-05-04 Delete hardware/frontpanel/gerber_files/frontpanel-F.CrtYd.gbr
    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
    [frontpanel-F.CrtYd.gbr]
2024-05-04 Delete hardware/frontpanel/gerber_files/frontpanel-F.Cu.gtl
    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
    [frontpanel-F.Cu.gtl]
2024-05-04 Delete hardware/frontpanel/gerber_files/frontpanel-F.Fab.gbr
    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
    [frontpanel-F.Fab.gbr]
2024-05-04 Delete hardware/frontpanel/gerber_files/frontpanel-F.Mask.gts
    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
    [frontpanel-F.Mask.gts]
2024-05-04 Delete hardware/frontpanel/gerber_files/frontpanel-F.Paste.gtp
    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
    [frontpanel-F.Paste.gtp]
2024-05-04 Delete hardware/frontpanel/gerber_files/frontpanel-F.SilkS.gto
    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
    [frontpanel-F.SilkS.gto]
2024-05-04 Add files via upload
    created with KiCad 6.0 on Debian 12.5
    [frontpanel-B_Courtyard.gbr, frontpanel-B_Cu.gbl, frontpanel-B_Fab.gbr, frontpanel-B_Mask.gbs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]
2024-05-05 Delete hardware/mystat_circuit_board/circuit_board_image.png
    replaced with new version from KiCad 6.0
2024-05-05 Add files via upload
    new schematics from KiCad 6.0
    [analog.kicad_sch, digital.kicad_sch, mystat.kicad_sch, power.kicad_sch]
2024-05-05 Delete hardware/mystat_circuit_board/kicad_files/analog.sch
    replaced with new version
    [analog.sch]
2024-05-05 Delete hardware/mystat_circuit_board/kicad_files/digital.sch
    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
    [digital.sch]
2024-05-05 Delete hardware/mystat_circuit_board/kicad_files/mystat.sch
    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
    [mystat.sch]
2024-05-05 Delete hardware/mystat_circuit_board/kicad_files/power.sch
    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
    [power.sch]
2024-05-05 Add files via upload
    new version from KiCad 6.0
    [mystat.kicad_pcb]
2024-05-05 Add files via upload
    minor changes in KiCad 6.0 so that design rules checkers completes without warnings
    [mystat-B_Courtyard.gbr, mystat-B_Cu.gbl, mystat-B_Fab.gbr, mystat-B_Mask.gbs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]
2024-05-05 Delete hardware/mystat_circuit_board/gerber_files/mystat-B_CrtYd.gbr
    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
    [mystat-B_CrtYd.gbr]
2024-05-05 Delete hardware/mystat_circuit_board/gerber_files/mystat-B_SilkS.gbo
    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
    [mystat-B_SilkS.gbo]
2024-05-05 Delete hardware/mystat_circuit_board/gerber_files/mystat-F_CrtYd.gbr
    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
    [mystat-F_CrtYd.gbr]
2024-05-05 Delete hardware/mystat_circuit_board/gerber_files/mystat-F_SilkS.gto
    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
    [mystat-F_SilkS.gto]
2024-05-05 Delete hardware/mystat_circuit_board/gerber_files/mystat.drl
    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
    [mystat.drl]
2024-05-07 Add files via upload
    Update to KiCad 7.0 from Debian bookworm backports
    [backpanel.kicad_pcb, backpanel.kicad_sch]
2024-05-07 Add files via upload
    Updated files produced by KiCad 7.0
    [backpanel-B_Courtyard.gbr, backpanel-B_Cu.gbl, backpanel-B_Fab.gbr, backpanel-B_Mask.gbs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]
2024-05-07 Add files via upload
    Updated files to KiCad 7.0 from Debian bookworm backports
    [frontpanel.kicad_pcb, frontpanel.kicad_sch]
2024-05-07 Add files via upload
    Updated to files produced from KiCad 7.0
    [frontpanel-B_Courtyard.gbr, frontpanel-B_Cu.gbl, frontpanel-B_Fab.gbr, frontpanel-B_Mask.gbs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]
2024-05-07 Add files via upload
    Minor re-routing tracks on PCB to pass KiCad 7.0 design rules checks
    [analog.kicad_sch, digital.kicad_sch, mystat.kicad_pcb, mystat.kicad_sch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]
2024-05-07 Add files via upload
    Updated version to pass KiCad 7.0 design rules checks
    [mystat-B_Courtyard.gbr, mystat-B_Cu.gbl, mystat-B_Fab.gbr, mystat-B_Mask.gbs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]
2024-05-07 Add files via upload
    Updated labels on schematics
    [analog.kicad_sch, digital.kicad_sch, mystat.kicad_sch, power.kicad_sch]
2024-05-07 Add files via upload
    Minor routing change and edit back silkscreen.
    [mystat.kicad_pcb]

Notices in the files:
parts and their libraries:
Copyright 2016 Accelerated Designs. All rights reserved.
